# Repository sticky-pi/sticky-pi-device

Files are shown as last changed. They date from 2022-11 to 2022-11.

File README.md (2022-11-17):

# Hardware  and Software for the [Sticky Pi](https://sticky-pi.github.io) devices

**This readme is intended for contributors and developers**. 
Instructions to assemble Sticky Pis are available on [our documentation](https://doc.sticky-pi.com/hardware.html)

----------------------------- 

## Directory structure

### `hardware/`
Schematics, 3d files Bill of materials and such.

### `software/` 
Contains files and tools to build the Sticky Pi OS.

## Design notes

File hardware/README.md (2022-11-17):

# Sticky Pi Hardware

* `BOM.csv` -- a bill of material containing the description of all parts used, as well as a suggestion of a provider. 
* `sticky_pi_hat/` -- One of the parts in the BOM is the Sticky Pi hat. This is our custom electronics and should be factory assembled. This directory contains the necessary KiCAD files and a BOM.
* `CAD/` -- 3d parts STL snapshots from our [Onshape repository](https://cad.onshape.com/documents/73922dc6e3c6d7006b309c14/w/7e4fb88a2e93b6adba33fd5a/e/438cef0dea4f2cfe3bf83d91)

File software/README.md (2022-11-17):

# Sticky Pi Software

We make a local image from the stock Archlinux operating system, 
then we transfer custom files on it before we use QEMU to spawn a virtual machine on this image. Once in the virtual machine, 
we install dependencies and continue the configuration of the virtual image. In the end. We compress the resulting image 
(YYYY-MM-dd_sticky_pi_rpi.img.gz) --that can be burnt and used directly. The whole process is orchestrated by a Makefile 

* `src` -- a small python package, `sticky_pi_device`, that will be installed on the Raspberry Pi
* `take_picture` -- a C program to take the picture (adapted from [raspistill](https://github.com/raspberrypi/userland/blob/master/host_applications/linux/apps/raspicam/))
* `.env` -- definition of environment variables used at build and runtime (e.g. directory location, camera setting, ...)
* `Makefile` -- A tool to build the full image of a Sticky Pi. Needs to be run as superuser under a linux system **at your own risks**.
* `os_stub/` -- a directory mapping files to be copied to the root of the pi OS
* `utils` -- a set of scripts used during the image building process
* `prototypes/` -- a directory for developers to, for instance, create mock devices 

To build the image:
```sh
sudo make all
```

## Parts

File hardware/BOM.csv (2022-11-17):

part | type | tag | number | price_per_device_CAD | description | note | provider | link
Pi zero W | off-the-shelf | pi_zero | 1 | 20 | The [Raspberry Pi Zero W](https://www.raspberrypi.com/products/raspberry-pi-zero-w/) microcomputer |  | canakit.com | https://www.canakit.com/raspberry-pi-zero.html?defpid=4307
Pi camera HQ | off-the-shelf | camera | 1 | 70 | The [Raspberry Pi High Quality Camera](https://www.raspberrypi.com/products/raspberry-pi-high-quality-camera/) |  | pishop.ca | https://www.pishop.ca/product/raspberry-pi-hq-camera/
8mm CS lens | off-the-shelf | lens | 1 | 30 | An 8mm Cs mount lens with manually-adjustable aperture and focus and a 50° horizontal field of view. |  | Arducam | https://www.arducam.com/product/arducam-cs-mount-lens-for-raspberry-pi-hq-camera-8mm-focal-length-with-manual-focus-and-adjustable-aperture/
32 GB SD card (5 units / pack) | off-the-shelf | sd_card | 1 | 5.6 | A micro sd card. 32GB should be enough, unless you retrieve the data from your Sticky Pi very infrequently (e.g. every other month). You need to [manually flash it](#_burn_sd_card) before inserting it into the [Raspberry Pi](#pi_zero) |  | amazon.ca | https://www.amazon.ca/KOOTION-Micro-10pcs-UHS-I-Memory/dp/B07XKX2NXP
15cm camera flex cable ( (HBV RPI 160 FPC) | off-the-shelf | flex_cable | 1 | 1 | A flexible cable to connect that connects the [camera](#camera) to the [Raspberry Pi](#pi_zero) |  | aliexpress.com | https://www.aliexpress.com/item/32947418836.html?spm=a2g0o.cart.0.0.5eaa3c001hHS8H&mp=1
Microscope slide (standard: 75 x 25 mm) | off-the-shelf | glass_slide | 1 | 0.25 | A microscope slide that you can cut manually to make a lens cover on the [front of the camera box](#cambox_front) |  | amazon.ca | https://www.amazon.ca/AmScope-BS-50P-Microscope-Ground-Pre-Cleand/dp/B00NYI4RSG
Zip tie 12in | off-the-shelf | zip_tie_long | 2 | 0.1 | A pair of long zip ties to attach the [temperature probe](#dht22) |  | amazon.ca | https://www.amazon.ca/gp/product/B08N4B3PWC/ref=ppx_yo_dt_b_asin_title_o08_s00?ie=UTF8&psc=1
Zip tie 4in | off-the-shelf | zip_tie_short | 1 | 0.1 | A small zip tie to secure the cable during the [lightbox assembly](#_build_lightbox) |  | amazon.ca | https://www.amazon.ca/gp/product/B09TQXR4LR/ref=ppx_yo_dt_b_asin_title_o01_s00?ie=UTF8&psc=1
Male PCB headers (2x20, 2.54mm) | off-the-shelf | header_male_2x20 | 1 | 0.5 | PCB headers to solder on the [Raspberry Pi](#pi_zero) | You might also be able to buy raspberry pis with presoldered headers | aliexpress.com | https://www.aliexpress.com/item/32878530745.html?pdp_ext_f=%7B%22sku_id%22%3A%2265640776223%22%7D
Male PCB headers (2x1, 2.54mm) | off-the-shelf | header_male_2x1 | 1 | 0 | PCB headers to solder on the testing slot of our [Raspberry Pi Hat](#pi_hat) | You can buy extra [2x20 headers](#header_male_2x20) and break them to 2x1. | aliexpress.com | https://www.aliexpress.com/item/32878530745.html?pdp_ext_f=%7B%22sku_id%22%3A%2265640776223%22%7D
11pin 2.54mm PCB Screw Terminal Blocks | off-the-shelf | terminal_block | 1 | 1 | Small terminal blocks to solder on the back of our [Raspberry Pi Hat](#pi_hat) |  | aliexpress.com | https://www.aliexpress.com/item/1005002453862004.html?spm=a2g0o.9042311.0.0.7ffa4c4dxnouy5
dht22 temperature humidity sensor | off-the-shelf | dht22 | 1 | 4 | A humidity and temperature sensor |  | aliexpress.com | https://www.aliexpress.com/item/32901733917.html?spm=a2g0s.9042311.0.0.13564c4dqiiNwk
8mm push button | off-the-shelf | push_button | 1 | 1.4 | A waterproof stainless steel push button to insert in the [back of the camera box](#cambox_back) |  | aliexpress.com | https://www.aliexpress.com/item/4000043687021.html?spm=a2g0s.9042311.0.0.10444c4dmVJAuf
5mm orange led (WP7113SECK) | off-the-shelf | led_orange | 1 | 0.5 | A bright orange LED to insert in the [back of the camera box](#cambox_back) |  | DigiKey | https://www.digikey.com/en/products/detail/kingbright/WP7113SECK-J3/4753660
M12x1.2 cable gland | off-the-shelf | cable_gland | 1 | 1 | A stainless steel cable gland to insert in the [back of the camera box](#cambox_back) |  | aliexpress.com | https://www.aliexpress.com/item/1005001952576665.html?spm=a2g0o.cart.0.0.f9233c00dhXaEx&mp=1
CR1220 Coin Cell | off-the-shelf | coin_cell | 1 | 0.5 | A small battery for our [Raspberry Pi Hat](#pi_hat). This is necessary for the clock to keep accurate time. The battery should last for several years (though we are currently testing this). |  | amazon.ca | https://www.amazon.ca/Murata-CR1220-Battery-Lithium-Coin/dp/B0857H2TT7
Silica desiccant bag | off-the-shelf | silica_bag | 2 | 0 | Silica bags to attach to the [Raspberry Pi sledge](#pi_sledge) to absorb moisture. |  | aliexpress.com | https://www.aliexpress.com/item/32772734661.html?spm=a2g0s.9042311.0.0.4cf04c4dv3gVAu
M3 x 20 self-tapping philips screws | off-the-shelf | screw_m3x20 | 4 | 0.1 | Screws to mount the [Raspberry Pi Zero](#pi_zero) and our [custom Raspberry Pi hat](#pi_hat) together on the [Raspberry Pi sledge](#pi_sledge). |  | aliexpress.com | https://www.aliexpress.com/item/32835249403.html?spm=a2g0s.9042311.0.0.27424c4dLTOcNH
M3 x 14 self-tapping philips screws | off-the-shelf | screw_m3x14 | 8 | 0.2 | Screws to lock the [back](#cambox_back) and [front](#cambox_front) of the camera box. |  | aliexpress.com | https://www.aliexpress.com/item/32835249403.html?spm=a2g0s.9042311.0.0.27424c4dLTOcNH
M3 x 6 self-tapping philips screws | off-the-shelf | screw_m3x6 | 10 | 0.1 | Screws to attach the [camera](#camera) to the [Raspberry Pi sledge](#pi_sledge), the [Raspberry Pi sledge](#pi_sledge) to the [back of the camera box](#cambox_back), and to mount the [DHT22](#dht22) in [its shell](#dht_shell) |  | aliexpress.com | https://www.aliexpress.com/item/32835249403.html?spm=a2g0s.9042311.0.0.27424c4dLTOcNH
M3 Stainless Acorn Nut Cap | off-the-shelf | nut_acorn_m3 | 8 | 0.4 | A set of acorn nuts to lock the [rods](#rod_m3x250) |  | aliexpress.com | https://www.aliexpress.com/item/32993886063.html?spm=a2g0o.cart.0.0.26443c00UEA2H1&mp=1
M3 x 250 threaded rods | off-the-shelf | rod_m3x250 | 4 | 5 | Four rods to serve as the "legs" that connect the lightbox to the camera box |  | aliexpress.com | https://www.aliexpress.com/item/4000990108860.html?spm=a2g0o.cart.0.0.79ae3c00cEblbO&mp=1
M3 nuts | off-the-shelf | nut_standard_m3 | 8 | 0 | A set of nuts to lock the [rods](#rod_m3x250) |  | aliexpress.com | https://www.aliexpress.com/item/32886183839.html?pdp_ext_f=%7B%22sku_id%22%3A%2265651913269%22%7D
2-pin automotive connector male | off-the-shelf | auto_connector | 1 | 0 | A weather-proof power connector | Buy male-female pairs and use the female for the battery | aliexpress.com | https://www.aliexpress.com/item/32801400952.html?spm=a2g0o.order_list.0.0.43281802B3HZ5R
Custom Pi hat | custom-ordered | pi_hat | 1 | 40 | Our custom Raspberry Pi hat. This board is factory-assembled. All the necessary files and schematics are available on our [GitHub repository](https://github.com/sticky-pi/sticky-pi-device/tree/main/hardware/sticky_pi_hat) |  | PCBWay
Camera front | 3d-printed | cambox_front | 1 | 0 | The front of the camera box |  | doc.sticky-pi.com | https://github.com/sticky-pi/sticky-pi-device/blob/main/hardware/CAD/cambox_front.stl
Camera back | 3d-printed | cambox_back | 1 | 0 | The back of the camera box |  | doc.sticky-pi.com | https://github.com/sticky-pi/sticky-pi-device/blob/main/hardware/CAD/cambox_back.stl
Camera tube | 3d-printed | cambox_tube | 1 | 0 | The core of the camera box |  | doc.sticky-pi.com | https://github.com/sticky-pi/sticky-pi-device/blob/main/hardware/CAD/cambox_tube.stl
Camera visor | 3d-printed | cambox_visor | 1 | 0 | The visor to help shelter the lens cover from light and water |  | doc.sticky-pi.com | https://github.com/sticky-pi/sticky-pi-device/blob/main/hardware/CAD/cambox_visor.stl
Raspberry pi sledge | 3d-printed | pi_sledge | 1 | 0 | The frame on which the electronics is mounted. It is housed in the camera box |  | doc.sticky-pi.com | https://github.com/sticky-pi/sticky-pi-device/blob/main/hardware/CAD/pi_sledge.stl
Standoff | 3d-printed | pi_standoff | 4 | 0 | Standoffs to securely attach the [Raspberry Pi Zero](#pi_zero) to the [custom board](#pi_hat) |  | doc.sticky-pi.com | https://github.com/sticky-pi/sticky-pi-device/blob/main/hardware/CAD/pi_standoff.stl
DHT22 shell | 3d-printed | dht_shell | 1 | 0 | An open enclosure to mount the [temperature and humidity sensor](#dht22) |  | doc.sticky-pi.com | https://github.com/sticky-pi/sticky-pi-device/blob/main/hardware/CAD/dht_shell.stl
Light box front | 3d-printed | lightbox_front | 1 | 0 | The front of the lightbox. It acts as a diffuser | It must be made of a transparent material | doc.sticky-pi.com | https://github.com/sticky-pi/sticky-pi-device/blob/main/hardware/CAD/lightbox_front.stl
Light box back | 3d-printed | lightbox_back | 1 | 0 | The back of the lightbox. It holds the LED light strips |  | doc.sticky-pi.com | https://github.com/sticky-pi/sticky-pi-device/blob/main/hardware/CAD/lightbox_back.stl
Drawer hook | 3d-printed | drawer_hook | 8 | 0 | A custom washer with a feature to retain the sticky trap drawer |  | doc.sticky-pi.com | https://github.com/sticky-pi/sticky-pi-device/blob/main/hardware/CAD/drawer_hook.stl

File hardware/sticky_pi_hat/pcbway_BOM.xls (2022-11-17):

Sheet: Sheet1
 |  |  | xxxx xxxx xxxxx xxPCS BOM (Sample Bill of Materials)
Item # | *Designator | *Qty | Manufacturer | *Mfg Part # | Description / Value | *Package/Footprint | Type | Your Instructions / Notes
1 | BT2 | 1 | Keystone Electronics | 3000 | Battery_Cell | SMD | SMD
2 | C2 | 1 | KEMET | C1206C104K8RAC7800 | 0.1μF | 1206 | SMD
3 | C1,C3,C4,C6 | 4 | Kyocera International Inc. Electronic Components | CM316X5R106K10AT | 10μF | 1206 | SMD
4 | C5 | 1 | Würth Elektronik | 865230640001 | 100nF | SMD | SMD
5 | C7 | 1 | Würth Elektronik | 865080242004 | 47uF | SMD | SMD
6 | D3,D4 | 2 | Micro Commercial Co | SM4001PL | SM4001PL | SOD-123F | SMD
7 | J2 | 1 | TE Connectivity AMP Connectors | 1-215307-3 | Conn_02x13_Odd_Even | thru-hole | thru-hole
8 | L1 | 1 | TDK Corporation | VLS3012HBX-2R2M | 2.2μH | Nonstandard | SMD
9 | Q2 | 1 | Alpha & Omega Semiconductor Inc. | AO3415A | AO3415A | SOT-23-3 | SMD
10 | Q1,Q3,Q4 | 3 | Infineon Technologies | BSS806NH6327XTSA1 | BSS806NH6327XTSA1 | SOT-23-3 | SMD
11 | R1,R10 | 2 | KOA Speer Electronics, Inc. | RK73H2HTTE7502F | 75k | 2010 | SMD
12 | R2 | 1 | YAGEO | AC2010JK-07560RL | 560Ω | 2010 | SMD
13 | R3 | 1 | KOA Speer Electronics, Inc. | RK73B2HTTE101J | 100Ω | 2010 | SMD
14 | R4 | 1 | Stackpole Electronics, Inc. | RMCF2010JT2K20 | 2.2k | 2010 | SMD
15 | R5-R7,R11,R12 | 5 | YAGEO | RC2010JK-0710KL | 10k | 2010 | SMD
16 | R8 | 1 | YAGEO | RC2010FK-075R49L | 5.49Ω | 2010 | SMD
17 | R9 | 1 | Vishay Dale | TNPW080549K9FHEA | 49.9k | 805 | SMD
18 | U2 | 1 | Texas Instruments | TPL5110 | TPL5110 | SOT-23-THIN | SMD
19 | U3 | 1 | Texas Instruments | TPS63002 | TPS63002 | 10-VSON | SMD
20 | U4 | 1 | Maxim Integrated | DS1307Z+ | DS1307Z+ | 8-SOIC | SMD
21 | U5 | 1 | Microchip Technology | MCP3001-I_ST | MCP3001-I_ST | 8-TSSOP | SMD
22 | Y1 | 1 | Micro Crystal AG | CM9V-T1A-32.768KHZ-12.5PF-20PPM-TA-QC | Crystal | 2-SMD | SMD

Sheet: Sheet2
BT2 | 1 | Battery_Cell | Keystone Electronics | 3000 | SMD
C2 | 1 | 0.1μF | KEMET | C1206C104K8RAC7800 | 1206
C1,C3,C4,C6 | 4 | 10μF | Kyocera International Inc. Electronic Components | CM316X5R106K10AT | 1206
C5 | 1 | 100nF | Würth Elektronik | 865230640001 | SMD
C7 | 1 | 47uF | Würth Elektronik | 865080242004 | SMD
D3,D4 | 2 | SM4001PL | Micro Commercial Co | SM4001PL | SOD-123F
J2 | 1 | Conn_02x13_Odd_Even | TE Connectivity AMP Connectors | 1-215307-3 | thru-hole
L1 | 1 | 2.2μH | TDK Corporation | VLS3012HBX-2R2M | Nonstandard
Q2 | 1 | AO3415A | Alpha & Omega Semiconductor Inc. | AO3415A | SOT-23-3
Q1,Q3,Q4 | 3 | BSS806NH6327XTSA1 | Infineon Technologies | BSS806NH6327XTSA1 | SOT-23-3
R1,R10 | 2 | 75k | KOA Speer Electronics, Inc. | RK73H2HTTE7502F | 2010
R2 | 1 | 560Ω | YAGEO | AC2010JK-07560RL | 2010
R3 | 1 | 100Ω | KOA Speer Electronics, Inc. | RC2010JK-0710KL | 2010
R4 | 1 | 2.2k | Stackpole Electronics, Inc. | RMCF2010JT2K20 | 2010
R5-R7,R11,R12 | 5 | 10k | YAGEO | RC2010JK-0710KL | 2010
R8 | 1 | 5.5Ω | YAGEO | RC2010FK-075R49L | 2010
R9 | 1 | 49.9k | Vishay Dale | TNPW080549K9FHEA | 805
U2 | 1 | TPL5110 | Texas Instruments | TPL5110 | SOT-23-THIN
U3 | 1 | TPS63002 | Texas Instruments | TPS63002 | 10-VSON
U4 | 1 | DS1307Z+ | Maxim Integrated | DS1307Z+ | 8-SOIC
U5 | 1 | MCP3001-I_ST | Microchip Technology |  | 8-TSSOP
Y1 | 1 | Crystal | Micro Crystal AG | CM9V-T1A-32.768KHZ-12.5PF-20PPM-TA-QC | 2-SMD

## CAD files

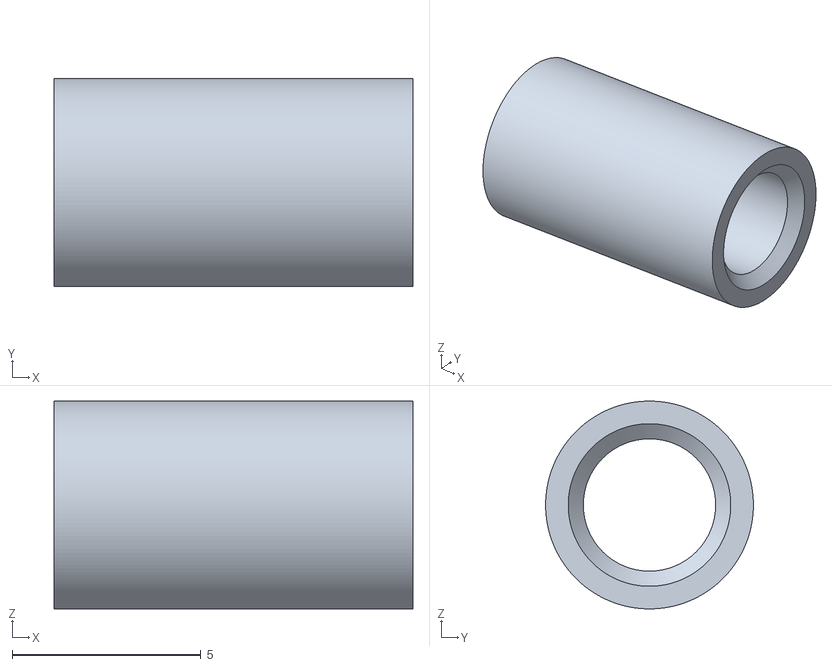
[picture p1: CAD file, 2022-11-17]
hardware/CAD/pi_standoff.stl
9.50 x 5.50 x 5.50

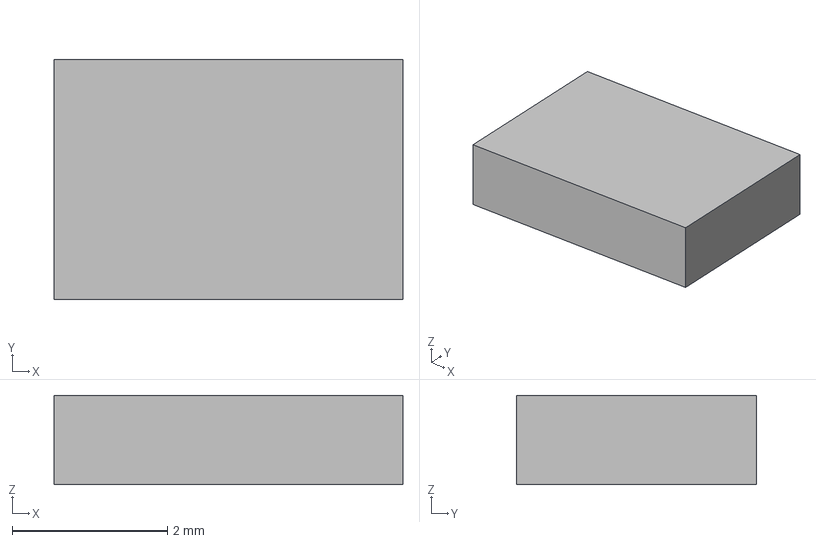
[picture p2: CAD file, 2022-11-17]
hardware/sticky_pi_hat/MCP3001/ST.step
4.50 x 3.10 x 1.15 mm

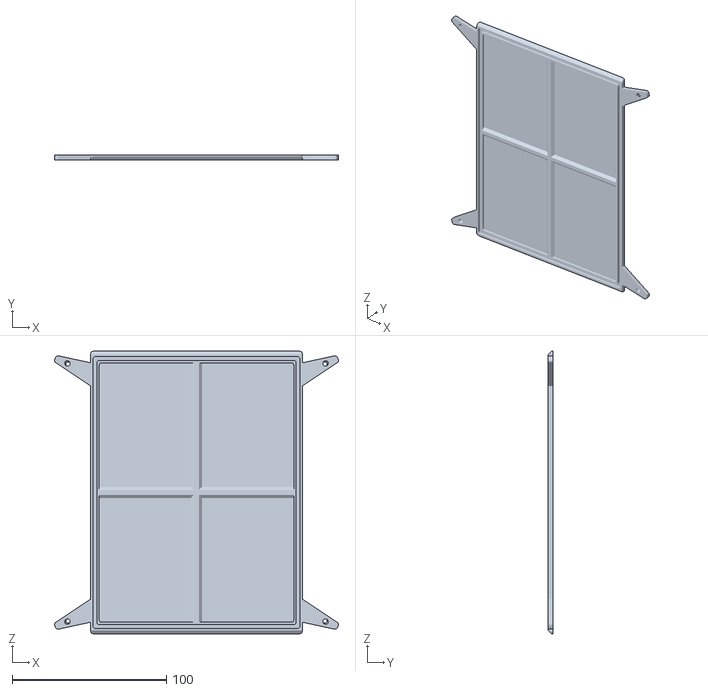
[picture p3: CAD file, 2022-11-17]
hardware/CAD/lightbox_lid.stl
184.0 x 3.00 x 183.0

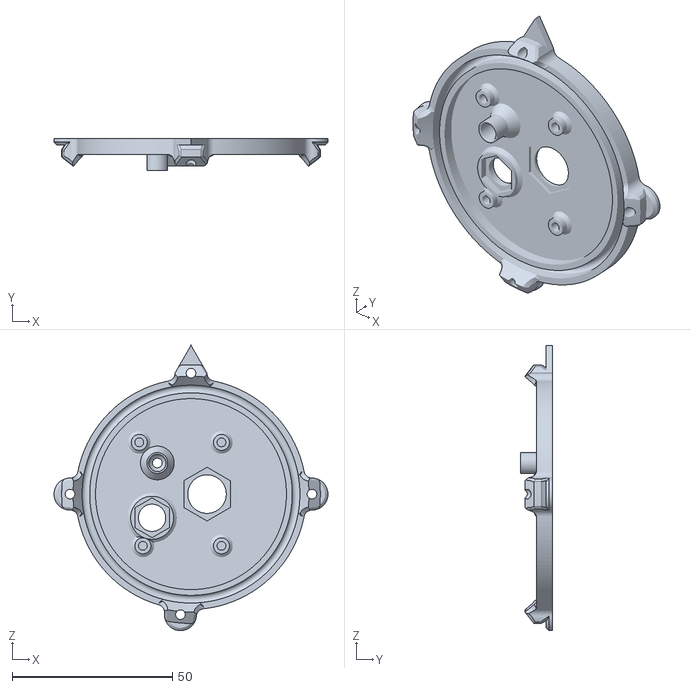
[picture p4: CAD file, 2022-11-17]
hardware/CAD/cambox_back.stl
85.4 x 10.0 x 88.9

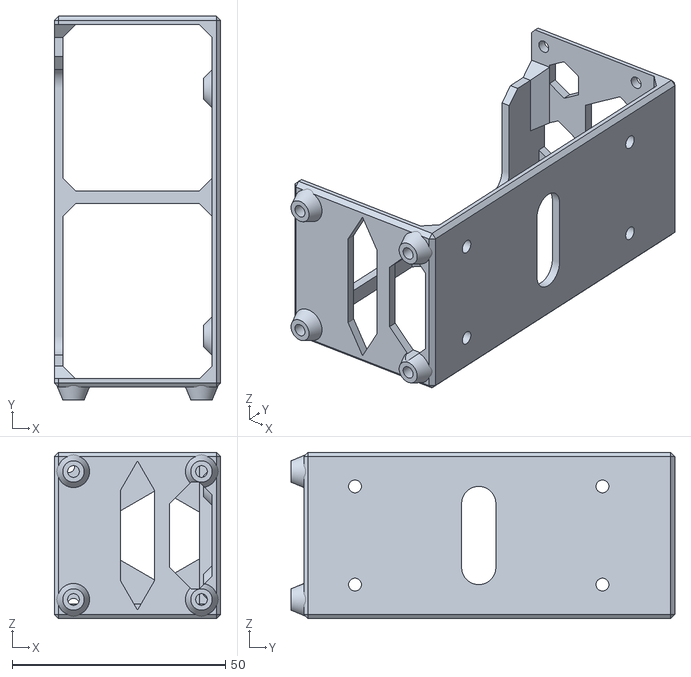
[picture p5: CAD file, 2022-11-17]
hardware/CAD/pi_sledge.stl
39.0 x 90.0 x 39.0

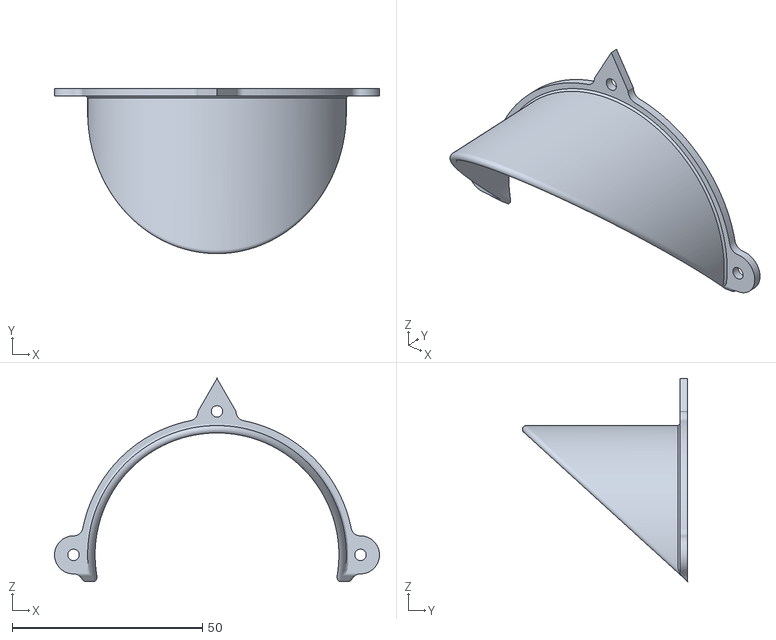
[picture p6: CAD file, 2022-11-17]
hardware/CAD/cambox_visor.stl
85.4 x 43.4 x 53.4

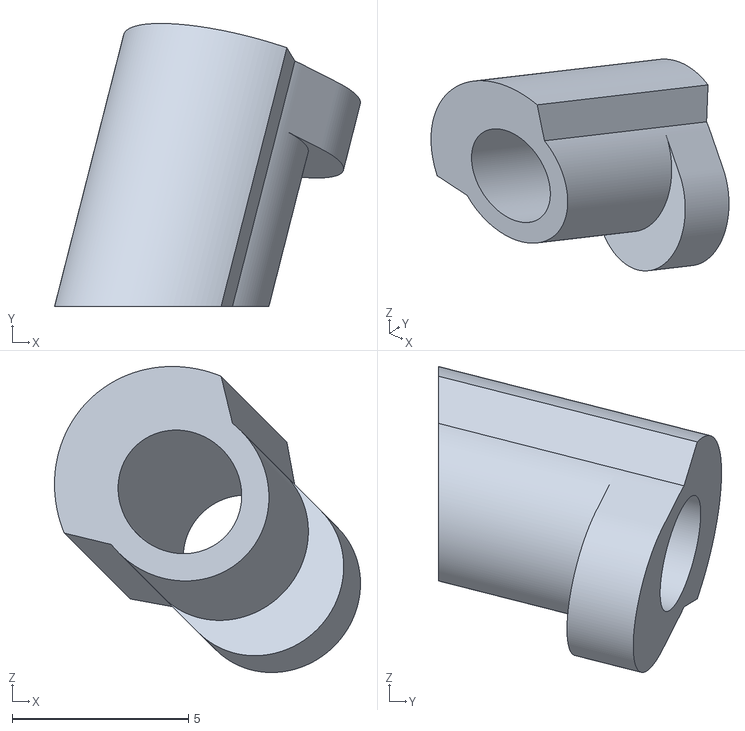
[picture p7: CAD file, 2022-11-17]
hardware/CAD/drawer_hook.stl
8.69 x 8.04 x 8.69

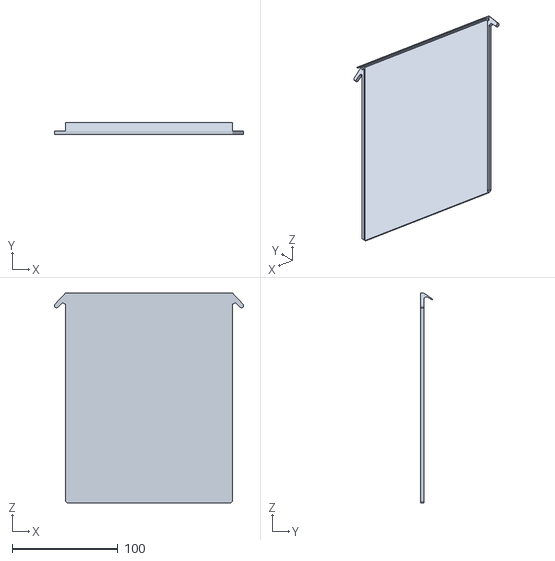
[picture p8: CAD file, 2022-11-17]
hardware/CAD/card_drawer.stl
179.4 x 11.0 x 199.0

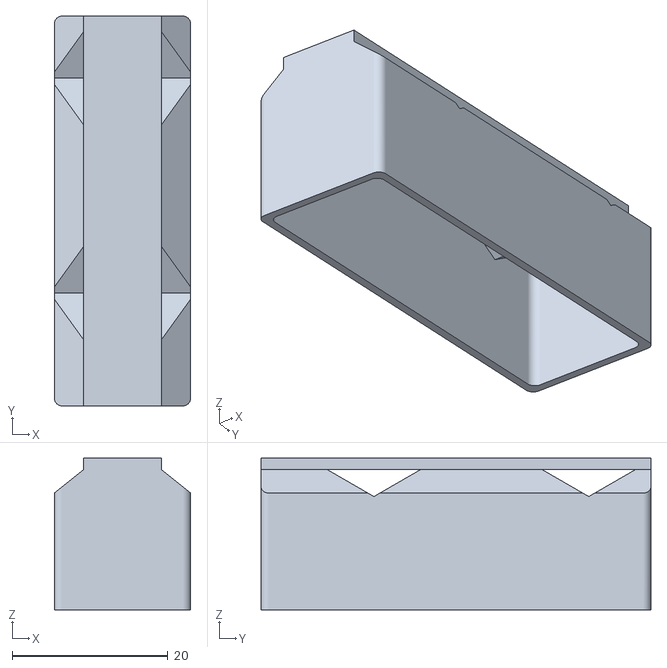
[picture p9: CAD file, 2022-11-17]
hardware/CAD/dht_shell.stl
17.5 x 50.0 x 19.5

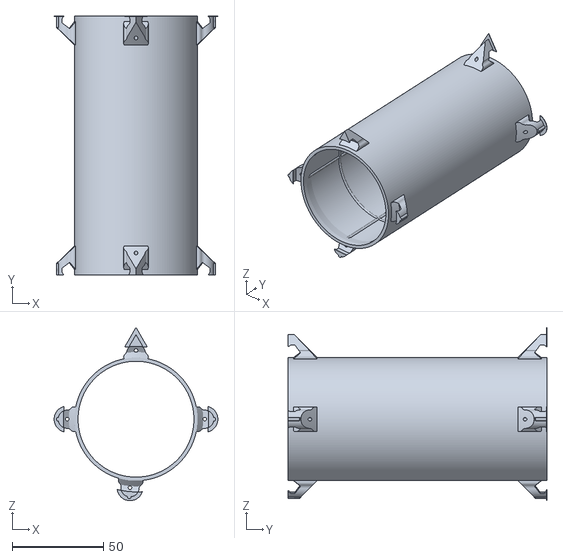
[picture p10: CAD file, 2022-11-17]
hardware/CAD/cambox_tube.stl
89.8 x 142.0 x 95.0

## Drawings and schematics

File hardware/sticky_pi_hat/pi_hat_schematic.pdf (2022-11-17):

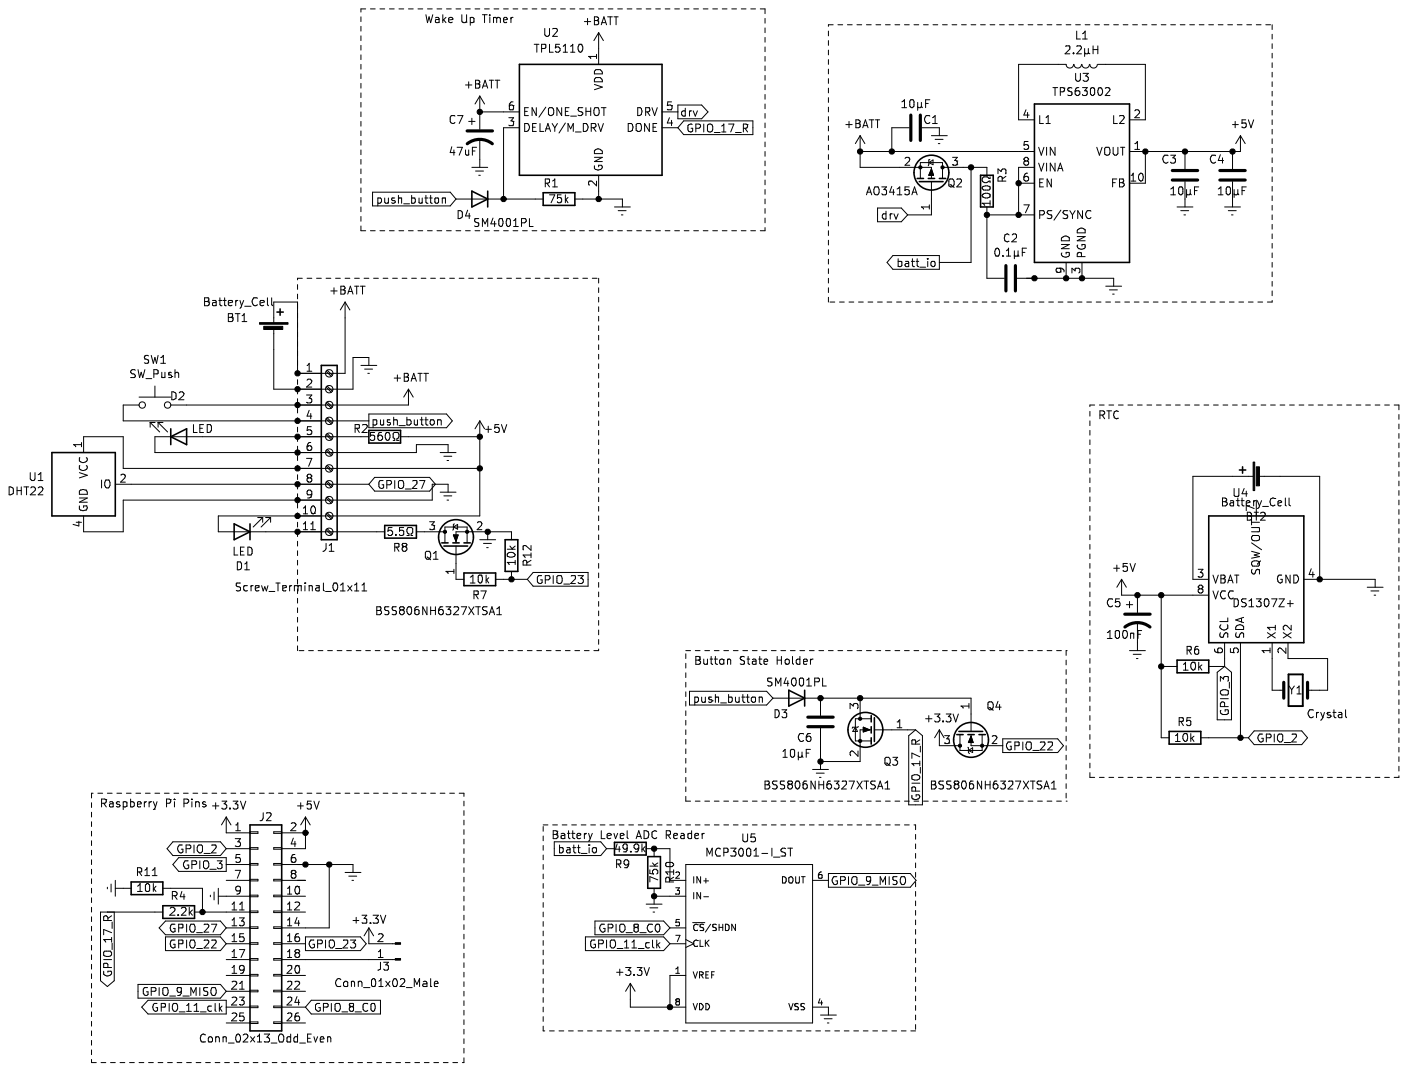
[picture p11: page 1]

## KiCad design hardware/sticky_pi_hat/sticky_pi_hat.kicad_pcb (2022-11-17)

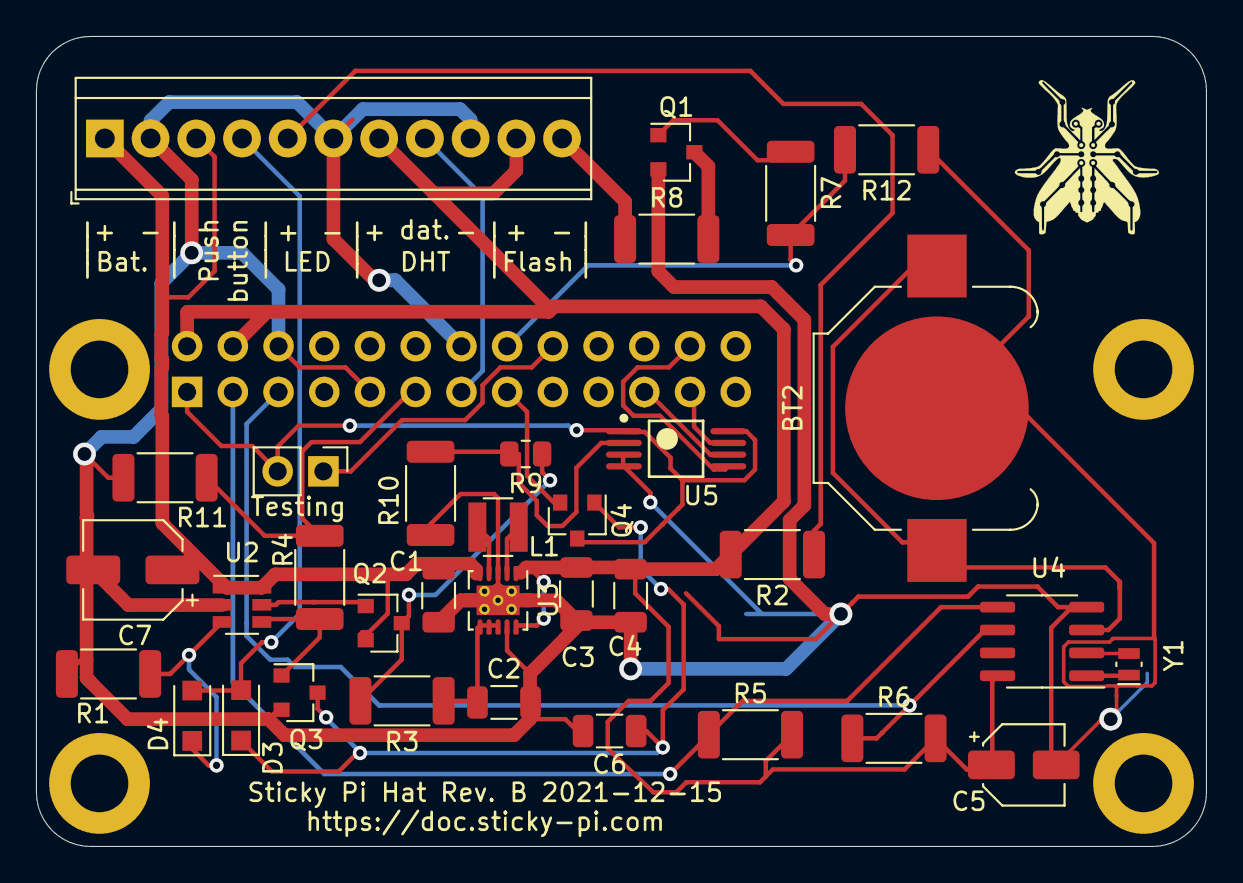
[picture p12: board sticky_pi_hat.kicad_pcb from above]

Board: 2 copper layers, 65.0 x 45.0 mm, 35 parts (1 on the bottom side), 31 nets.

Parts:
BT2: Battery_Cell; BatteryHolder_Keystone_3000_1x12mm
C1, C3, C4, C6: 10μF; C_1206_3216Metric
C2: 0.1μF; C_1206_3216Metric
C5: 100nF; CP_Elec_4x4.5
C7: 47uF; CP_Elec_5x5.3
D3, D4: SM4001PL; D_SOD-123F
J1: Screw_Terminal_01x11; TerminalBlock_TE_1-282834-1_1x11_P2.54mm_Horizontal
J2: Conn_02x13_Odd_Even; PinSocket_2x13_P2.54mm_Vertical
J3: Conn_01x02_Male; PinHeader_1x02_P2.54mm_Vertical
L1: 2.2μH; L_Abracon_ASPI-3012S
Q1, Q3, Q4: BSS806NH6327XTSA1; SOT-23
Q2: AO3415A; SOT-23
R1, R10: 75k; R_2010_5025Metric
R2: 560Ω; R_2010_5025Metric
R3: 100Ω; R_2010_5025Metric
R4: 2.2k; R_2010_5025Metric
R5, R6, R7, R11, R12: 10k; R_2010_5025Metric
R8: 5.5Ω; R_2010_5025Metric
R9: 49.9k; R_0805_2012Metric
U2: TPL5110; SOT-23-6
U3: TPS63002; Texas_DSC0010J_ThermalVias
U4: DS1307Z+; SOIC-8_3.9x4.9mm_P1.27mm
U5: MCP3001-I_ST; Microchip-MCP3001-I_ST-Level_A
Y1: Crystal; Crystal_SMD_MicroCrystal_CM9V-T1A-2Pin_1.6x1.0mm

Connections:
+3V3: J2.1, J3.2, Q4.3, U5.1, U5.8
+5V: C3.1, C4.1, C5.1, J1.7, J1.10, J2.2, J2.4, R2.2, R5.2, R6.2, U3.1, U3.10, U4.8
+BATT: C1.1, C7.1, J1.1, J1.3, Q2.2, U2.1, U2.6, U3.5
Earth: BT2.2, C1.2, C2.1, C3.2, C4.2, C5.2, C6.2, C7.2, J1.2, J1.6, J1.9, J2.6, J2.9, J2.14, Q1.2, Q3.2, R1.2, R10.2, R11.2, R12.1, U2.2, U3.3, U3.9, U3.11, U4.4, U5.3, U5.4
GPIO_2: J2.3, R5.1, U4.5
GPIO_3: J2.5, R6.1, U4.6
GPIO_8_C0: J2.24, U5.5
GPIO_9_MISO: J2.21, U5.6
GPIO_11_clk: J2.23, U5.7
GPIO_17_R: Q3.1, R4.1, U2.4
GPIO_22: J2.15, Q4.2
GPIO_23: J2.16, R7.2, R12.2
GPIO_27: J1.8, J2.13
unnamed: BT2.1, U4.3
unnamed: C2.2, R3.1, U3.6, U3.7, U3.8
unnamed: C6.1, D3.1, Q3.3, Q4.1
unnamed: J1.11, R8.1
unnamed: J1.5, R2.1
unnamed: D4.1, R1.1, U2.3
unnamed: J2.11, R4.2, R11.1
unnamed: J2.18, J3.1
unnamed: L1.1, U3.2
unnamed: L1.2, U3.4
unnamed: Q1.1, R7.1
unnamed: Q1.3, R8.2
unnamed: R9.2, R10.1, U5.2
unnamed: U4.1, Y1.1
unnamed: U4.2, Y1.2
batt_io: Q2.3, R3.2, R9.1
drv: Q2.1, U2.5
push_button: D3.2, D4.2, J1.4

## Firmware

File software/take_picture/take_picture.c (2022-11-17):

/*
Copyright (c) 2018, Raspberry Pi (Trading) Ltd.
Copyright (c) 2013, Broadcom Europe Ltd.
Copyright (c) 2013, James Hughes
All rights reserved.

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
THIS SOFTWARE IS PROVIDED BY THE COPYRIGHT HOLDERS AND CONTRIBUTORS "AS IS" AND
ANY EXPRESS OR IMPLIED WARRANTIES, INCLUDING, BUT NOT LIMITED TO, THE IMPLIED
WARRANTIES OF MERCHANTABILITY AND FITNESS FOR A PARTICULAR PURPOSE ARE
DISCLAIMED. IN NO EVENT SHALL THE COPYRIGHT HOLDER OR CONTRIBUTORS BE LIABLE FOR ANY
DIRECT, INDIRECT, INCIDENTAL, SPECIAL, EXEMPLARY, OR CONSEQUENTIAL DAMAGES
(INCLUDING, BUT NOT LIMITED TO, PROCUREMENT OF SUBSTITUTE GOODS OR SERVICES;
LOSS OF USE, DATA, OR PROFITS; OR BUSINESS INTERRUPTION) HOWEVER CAUSED AND
ON ANY THEORY OF LIABILITY, WHETHER IN CONTRACT, STRICT LIABILITY, OR TORT
(INCLUDING NEGLIGENCE OR OTHERWISE) ARISING IN ANY WAY OUT OF THE USE OF THIS
SOFTWARE, EVEN IF ADVISED OF THE POSSIBILITY OF SUCH DAMAGE.
*/

/**
 * \file RaspiStill.c
 * Command line program to capture a still frame and encode it to file.
 * Also optionally display a preview/viewfinder of current camera input.
 *
 * Description
 *
 * 3 components are created; camera, preview and JPG encoder.
 * Camera component has three ports, preview, video and stills.
 * This program connects preview and stills to the preview and jpg
 * encoder. Using mmal we don't need to worry about buffers between these
 * components, but we do need to handle buffers from the encoder, which
 * are simply written straight to the file in the requisite buffer callback.
 *
 * We use the RaspiCamControl code to handle the specific camera settings.
 */

// We use some GNU extensions (asprintf, basename)
#ifndef _GNU_SOURCE
#define _GNU_SOURCE
#endif

#include <stdio.h>
#include <stdlib.h>
#include <ctype.h>
#include <string.h>
#include <memory.h>
#include <unistd.h>
#include <errno.h>
#include <sysexits.h>
#include <assert.h>
#include <stdarg.h>
#include <sys/types.h>
#include <sys/stat.h>
#include <sys/time.h>
#include <sys/statvfs.h>
#include <math.h>

#include "bcm_host.h"
#include "interface/vcos/vcos.h"

#include "interface/mmal/mmal.h"
#include "interface/mmal/mmal_logging.h"
#include "interface/mmal/mmal_buffer.h"
#include "interface/mmal/util/mmal_util.h"
#include "interface/mmal/util/mmal_util_params.h"
#include "interface/mmal/util/mmal_default_components.h"
#include "interface/mmal/util/mmal_connection.h"
#include "interface/mmal/mmal_parameters_camera.h"


#include "RaspiCamControl.h"
#include "RaspiPreview.h"
#include "RaspiHelpers.h"
#include "jsmn.h"
#include "DHT22.h"


#include <semaphore.h>
#include <math.h>
#include <pthread.h>
#include <time.h>
#include <wiringPi.h>

// Standard port setting for the camera component
#define MMAL_CAMERA_PREVIEW_PORT 0
#define MMAL_CAMERA_VIDEO_PORT 1
#define MMAL_CAMERA_CAPTURE_PORT 2

// Stills format information
// 0 implies variable
#define STILLS_FRAME_RATE_NUM 0
#define STILLS_FRAME_RATE_DEN 1

/// Video render needs at least 2 buffers.
#define VIDEO_OUTPUT_BUFFERS_NUM 3

#define MAX_EXIF_PAYLOAD_LENGTH 128
#define MAX_EXIF_LONG_PAYLOAD_LENGTH 256

#define CAMERA_NUM 0
#define SENSOR_MODE 0


/// Amount of time before first image taken to allow settling of
/// exposure etc. in milliseconds.
#define CAMERA_SETTLE_TIME       1000
struct stat st = {0};


int spi_im_w, spi_im_h, spi_im_jpeg_quality;
//                              0  1  2  3  4   5   6   7   8   9  10  11  12  13  14  15 16
int GPIO_TO_WIRING_PI_MAP[]= {30, 31, 8, 9, 7, 21, 22, 11, 10, 13, 12, 14, 26, 23, 15, 16, 27, 0, 1, 24, 28, 29, 3, 4, 5, 6, 25, 2};

#define CUSTOM_EXIF_KEY "EXIF.UserComment"

//#define CUSTOM_EXIF_HEADER "ver,temp,hum,bat,lum,lat,lng,alt,last-sync,b"
#define CUSTOM_EXIF_HEADER "v,T,H,B,L,lat,lng,a,l,b"
#define CUSTOM_EXIF_FORMAT "%s,%.1f,%.1f,%i,%.2f,%.5f,%.5f,%.1f,%s,%i"
#define CUSTOM_EXIF_TEMPLATE CUSTOM_EXIF_KEY "=" CUSTOM_EXIF_HEADER "\n" CUSTOM_EXIF_FORMAT


/** Structure containing all state information for the current run
 */
typedef struct
{
//   RASPICOMMONSETTINGS_PARAMETERS common_settings;     /// Common settings
   char camera_name[MMAL_PARAMETER_CAMERA_INFO_MAX_STR_LEN]; // Name of the camera sensor

   struct tm *timeinfo;
   char *linkname;                     /// filename of output file

     float temp; //4
     float  hum; // 4
     int bat; // 4
     int button; // 1 (0 or 1)

     float alt; //4
     double lng; // 8
     double lat; // 8

    float lum;
    char last_sync[20];


   MMAL_FOURCC_T encoding;             /// Encoding to use for the output file.
   int restart_interval;               /// JPEG restart interval. 0 for none.
   RASPIPREVIEW_PARAMETERS preview_parameters;    /// Preview setup parameters
   RASPICAM_CAMERA_PARAMETERS camera_parameters; /// Camera setup parameters
   MMAL_COMPONENT_T *camera_component;    /// Pointer to the camera component
   MMAL_COMPONENT_T *encoder_component;   /// Pointer to the encoder component
   MMAL_COMPONENT_T *null_sink_component; /// Pointer to the null sink component
   MMAL_CONNECTION_T *preview_connection; /// Pointer to the connection from camera to preview
   MMAL_CONNECTION_T *encoder_connection; /// Pointer to the connection from camera to encoder
   MMAL_POOL_T *encoder_pool; /// Pointer to the pool of buffers used by encoder output port
} RASPISTILL_STATE;

/** Struct used to pass information in encoder port userdata to callback
 */
typedef struct
{
   FILE *file_handle;                   /// File handle to write buffer data to.
   VCOS_SEMAPHORE_T complete_semaphore; /// semaphore which is posted when we reach end of frame (indicates end of capture or fault)
   RASPISTILL_STATE *pstate;            /// pointer to our state in case required in callback
} PORT_USERDATA;

// function prototypes
static MMAL_STATUS_T   add_custom_exif_field(RASPISTILL_STATE *state);
static void logging_error( char * pattern, ...);
static void logging( char * pattern, ...);


/**
 * Assign a default set of parameters to the state passed in
 *
 * @param state Pointer to state structure to assign defaults to
 */

static void default_status(RASPISTILL_STATE *state, struct tm *timeinfo)
{
   if (!state)
   {
      vcos_assert(0);
      return;
   }
   memset(state, 0, sizeof(*state));
   strncpy(state->camera_name, "(Unknown)", MMAL_PARAMETER_CAMERA_INFO_MAX_STR_LEN);


    state->temp=-300;
    state->hum -1;
    state->bat = -1;
    state->lum = 0.0;
    state->lat = 0.0;
    state->lng = 0.0;
    state->alt = 0.0;
    strncpy(state->last_sync, "2000-01-01 00:00:00", 20);

   state->timeinfo = timeinfo;
   state->linkname = NULL;
   state->camera_component = NULL;
   state->encoder_component = NULL;
   state->preview_connection = NULL;
   state->encoder_connection = NULL;
   state->encoder_pool = NULL;
   state->encoding = MMAL_ENCODING_JPEG;

   // Setup preview window defaults
   state->preview_parameters.wantFullScreenPreview = 0;
   state->preview_parameters.preview_component = NULL;
   state->preview_parameters.display_num = -1;


   raspicamcontrol_set_defaults(&state->camera_parameters);
   state->camera_parameters.roi.x = atoi(SPI_ZOOM_X);
   state->camera_parameters.roi.y = atoi(SPI_ZOOM_Y);
   state->camera_parameters.roi.w = atoi(SPI_ZOOM_W);
   state->camera_parameters.roi.h = atoi(SPI_ZOOM_H);

}

/**
 * Dump image state parameters to stderr. Used for debugging
 *
 * @param state Pointer to state structure to assign defaults to
 */
static void dump_status(RASPISTILL_STATE *state)
{
   int i;

   if (!state)
   {
      vcos_assert(0);
      return;
   }


   fprintf(stderr, "Link to latest frame enabled ");
   if (state->linkname)
   {
      fprintf(stderr, " yes, -> %s\n", state->linkname);
   }
   else
   {
      fprintf(stderr, " no\n");
   }
   fprintf(stderr, "\n\n");

   raspicamcontrol_dump_parameters(&state->camera_parameters);
}

static void encoder_buffer_callback(MMAL_PORT_T *port, MMAL_BUFFER_HEADER_T *buffer)
{
   int complete = 0;

   // We pass our file handle and other stuff in via the userdata field.

   PORT_USERDATA *pData = (PORT_USERDATA *)port->userdata;

   if (pData)
   {
      int bytes_written = buffer->length;

      if (buffer->length && pData->file_handle)
      {
         mmal_buffer_header_mem_lock(buffer);

         bytes_written = fwrite(buffer->data, 1, buffer->length, pData->file_handle);

         mmal_buffer_header_mem_unlock(buffer);
      }

      // We need to check we wrote what we wanted - it's possible we have run out of storage.
      if (bytes_written != buffer->length)
      {
         vcos_log_error("Unable to write buffer to file - aborting");
         complete = 1;
      }

      // Now flag if we have completed
      if (buffer->flags & (MMAL_BUFFER_HEADER_FLAG_FRAME_END | MMAL_BUFFER_HEADER_FLAG_TRANSMISSION_FAILED))
         complete = 1;
   }
   else
   {
      vcos_log_error("Received a encoder buffer callback with no state");
   }

   // release buffer back to the pool
   mmal_buffer_header_release(buffer);

   // and send one back to the port (if still open)
   if (port->is_enabled)
   {
      MMAL_STATUS_T status = MMAL_SUCCESS;
      MMAL_BUFFER_HEADER_T *new_buffer;

      new_buffer = mmal_queue_get(pData->pstate->encoder_pool->queue);

      if (new_buffer)
      {
         status = mmal_port_send_buffer(port, new_buffer);
      }
      if (!new_buffer || status != MMAL_SUCCESS)
         vcos_log_error("Unable to return a buffer to the encoder port");
   }

   if (complete)
      vcos_semaphore_post(&(pData->complete_semaphore));
}
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

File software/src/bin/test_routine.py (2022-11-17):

#!/bin/python

import time
import datetime
import os
import logging
from sticky_pi_device.utils import device_id
import RPi.GPIO as GPIO  # import RPi.GPIO module
import Adafruit_DHT
import subprocess
import picamera


# todo

# 1. test camera should show light intensity and keep light on
# 2. test camera in darkness!!

# 3. sync optimisation?
# 4. pull down resistor to so we can test without a pi?
# 5. file list faster? | make file index? faster than glob?

def test_flash():
    logging.info("Blinking flash 10 times")
    SPI_FLASH_GPIO = int(os.environ["SPI_FLASH_GPIO"])
    GPIO.setup(SPI_FLASH_GPIO, GPIO.OUT)  # set a port/pin as an output
    try:
        for i in range(10):
            GPIO.output(SPI_FLASH_GPIO, 1)
            time.sleep(0.05)
            GPIO.output(SPI_FLASH_GPIO, 0)
            time.sleep(.5)
    finally:
        logging.info("Turning flash off")
        GPIO.output(SPI_FLASH_GPIO, 0)


def test_turn_off():
    logging.info("Turning off")
    SPI_OFF_GPIO = int(os.environ["SPI_OFF_GPIO"])
    GPIO.setup(SPI_OFF_GPIO, GPIO.OUT)  # set a port/pin as an output
    GPIO.output(SPI_OFF_GPIO, 1)


def test_dht():
    logging.info("Reading DHT")
    sensor = os.environ["SPI_DHT"]
    pin = int(os.environ["SPI_DHT_GPIO"])
    supported_sensors = {'dht11': Adafruit_DHT.DHT11, 'dht22': Adafruit_DHT.DHT22}
    assert sensor in supported_sensors, "Unsupported sensor name: %s" % sensor
    sensor = supported_sensors[sensor]
    humidity, temperature = None, None
    try:
        humidity, temperature = Adafruit_DHT.read_retry(sensor, pin, retries=20, delay_seconds=.25)
    except Exception as e:
        logging.error(e, exc_info=True)
    out = {'temp': temperature,
           'hum': humidity}

    logging.info("DHT reads      : " + str(out))


def test_batt():
    logging.info("Reading battery through MCP3001")
    CLK = 11
    CS = 8
    MISO = 9

    GPIO.setup(CLK, GPIO.OUT)
    GPIO.setup(CS, GPIO.OUT)
    GPIO.setup(MISO, GPIO.IN)
    out_sum = 0
    for i in range(8):
        GPIO.output(CLK, False)  # CLK low
        GPIO.output(CS, True)  # /CS high
        GPIO.output(CS, False)  # /CS low

        lout = []
        for i in range(2):
            GPIO.output(CLK, True)
            GPIO.output(CLK, False)
            time.sleep(.01)
            v = GPIO.input(MISO)
            lout.append(v)

        out = 0
        for i in range(10):
            GPIO.output(CLK, True)
            GPIO.output(CLK, False)
            v = GPIO.input(MISO)
            lout.append(v)
            out <<= 1
            if v:
                out |= 0x1
        out_sum += out
        GPIO.output(CS, True)  # /CS high

    logging.info("Battery level  : " + str(out_sum / 8.0))
    time.sleep(.2)
    return 0


def test_push_button():
    SPI_MANUAL_ON_GPIO = int(os.environ["SPI_MANUAL_ON_GPIO"])
    GPIO.setup(SPI_MANUAL_ON_GPIO, GPIO.IN)  # set a port/pin as an output
    if GPIO.input(SPI_MANUAL_ON_GPIO):
        logging.info("Device was turned on with push button")
        return
    logging.info("Waiting for push button. Please press")
    while not GPIO.input(SPI_MANUAL_ON_GPIO):
        time.sleep(.2)


if __name__ == '__main__':

    GPIO.setmode(GPIO.BCM)

    logger = logging.getLogger()

    logger.setLevel(logging.INFO)

    logging.info("------------- TESTING INFO -------------")
    logging.info("Device ID: " + device_id())
    time.sleep(2)
    logging.info("Time     : " + str(datetime.datetime.now()))
    time.sleep(2)
    logging.info("Partitions     :\n" + subprocess.check_output("df -h", shell=True).decode())
    time.sleep(2)
    # ==============================================================

    logging.info("------------- TESTING PERIPHERALS -------------")
    test_flash()
    time.sleep(2)
    test_dht()
    time.sleep(2)
    test_batt()

    logging.info("------------- TESTING PUSH BUTTON-------------")
    time.sleep(2)
    test_push_button()

    # ==============================================================

    logging.info("------------- CAMERA TESTING AND CALIBRATION -------------")
    import tempfile

    tmp_image = tempfile.mktemp(suffix=".jpg")
    no_qr_code_at_least_once = False
    done = False

    with picamera.PiCamera() as camera:
        logging.info("Now manually setting up camera zoom/focus/aperture")
        logging.info("Add the QR code when done")
        time.sleep(2.0)
        camera.framerate = 10
        camera.resolution = (int(os.environ["SPI_IM_W"]), int(os.environ["SPI_IM_H"]))
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

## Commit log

2020-11-04 populate device
    [BOM.csv, main.fzz, main_contour.gm1, main_copperBottom.gbl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]
2021-02-17 clean up BOM
    [BOM.csv, main.fzz]
2021-04-15 almost there with refactory of device
2021-04-30 various changes for new camera, wifi harvester and packaging
2021-05-11 update BOM
    [BOM.csv]
2021-05-18 improve device firt boot script and misc
2021-09-15 new pi hat
    [main.fzz, sticky_pi_hat-B_Cu.gbr, sticky_pi_hat-B_Mask.gbr, sticky_pi_hat-B_Paste.gbr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]
2021-09-15 clean-up old hardware
    [main_contour.gm1, main_copperBottom.gbl, main_copperTop.gtl, main_maskBottom.gbs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]
2021-09-26 fix PCB issues
2021-10-14 Add P-channel mosfet to tpl5110
    [sticky_pi_hat.kicad_pcb, sticky_pi_hat.sch]
2021-12-15 add external pull down resistor to flash and push button outputs
    [sticky_pi_hat.kicad_pcb, sticky_pi_hat.sch]
2021-12-16 add diode to prevent wrong measurement of R1(timing) dut to pushbutton state holder
    [sticky_pi_hat.kicad_pcb, sticky_pi_hat.sch]
2022-02-04 hardware updates
    [BOM.csv, cambox_back.stl, cambox_tube.stl, cambox_visor.stl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]
2022-03-04 optional wpa setup to get time from net on first boot, in case harvester is absent
2022-03-30 device wifi update
2022-03-31 add mock device status
2022-04-19 much progress on device
2022-05-11 fix bug when no space is left on device. Fix bug when adding several persistent ssid with the same name
2022-06-02 update CAD
    [cambox_back.stl, cambox_tube.stl, cambox_visor.stl, dht_shell.stl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]
2022-07-31 bom update
    [BOM.csv]
2022-07-31 mock server to test deta harvesting without a device
